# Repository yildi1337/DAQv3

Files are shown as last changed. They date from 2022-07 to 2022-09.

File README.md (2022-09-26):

# DAQv3
A Dual-Channel, Low Noise, Modular, 100 kHz Bandwidth, 24-Bit Data Acquisition (DAQ) Device / FFT Signal Analyzer

# Table of Contents

- **[Introduction](#introduction)**
- **[CAD Model](#cad-model)**
- **[Modules](#modules)**
  - [AnalogConversion_v1](#AnalogConversion_v1)
  - [AnalogConversion_v2](#AnalogConversion_v2)
  - [AnalogConversion_v3](#AnalogConversion_v3)
  - [Backplane_v1](#Backplane_v1)
  - [DigitalBackend_v1](#DigitalBackend_v1)
  - [PowerSupply_5V_v1](#PowerSupply_5V_v1)
  - [PowerSupply_5V_v2](#PowerSupply_5V_v2)
  - [PowerSupply_12V_v1](#PowerSupply_12V_v1)
  - [PowerSupply_12V_v2](#PowerSupply_12V_v2)
  - [USBConnectors_v1](#USBConnectors_v1)
- **[Firmware](#firmware)**
- **[USB Driver](#usb-driver)**
- **[Debug and Control Interface](#debug-and-control-interface)**
- **[Measurement Results](#measurement-results)**
  - [Linear Power Supply vs. Switched-Mode Power Supply](#linear-power-supply-vs-switched-mode-power-supply)
  - [Differential Input Module (AnalogConversion_v3)](#differential-input-module-analogconversion_v3)

# Introduction

Work in progress ...

# CAD Model

The complete CAD model can be downloaded <a href="https://github.com/yildi1337/DAQv3/tree/main/cad_complete/inventor">here</a> (Autodesk Inventor 2023 files) including all <a href="#modules">modules</a> and the case.

<p align="center">
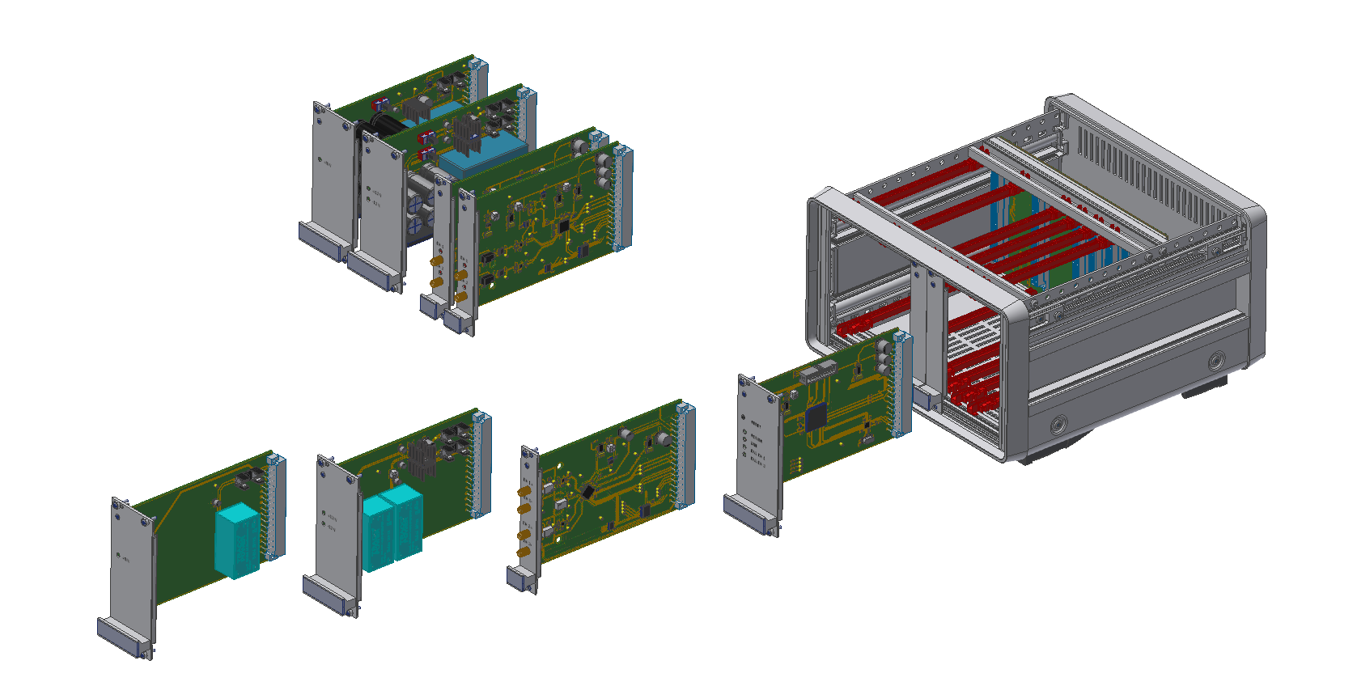
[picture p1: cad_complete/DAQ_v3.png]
    
</p>

# Modules

## AnalogConversion_v1

- [Schematics (PDF)](https://github.com/yildi1337/DAQv3/blob/main/schematics/AnalogConversion_v1_Schematics.pdf)
- [Schematics (Eagle)](https://github.com/yildi1337/DAQv3/blob/main/eagle/AnalogConversion_v1.sch)
- [Board (Eagle)](https://github.com/yildi1337/DAQv3/blob/main/eagle/AnalogConversion_v1.brd)
- [Gerber Files](https://github.com/yildi1337/DAQv3/blob/main/pcb_gerber/AnalogConversion_v1_2022-03-20.zip)
- [3D Step File](https://github.com/yildi1337/DAQv3/blob/main/cad_modules_step/AnalogConversion_v1.step)
- [Bill of Materials](https://github.com/yildi1337/DAQv3/blob/main/pcb_bom/BOM_AnalogConversion_v1.txt)

<p align="center">
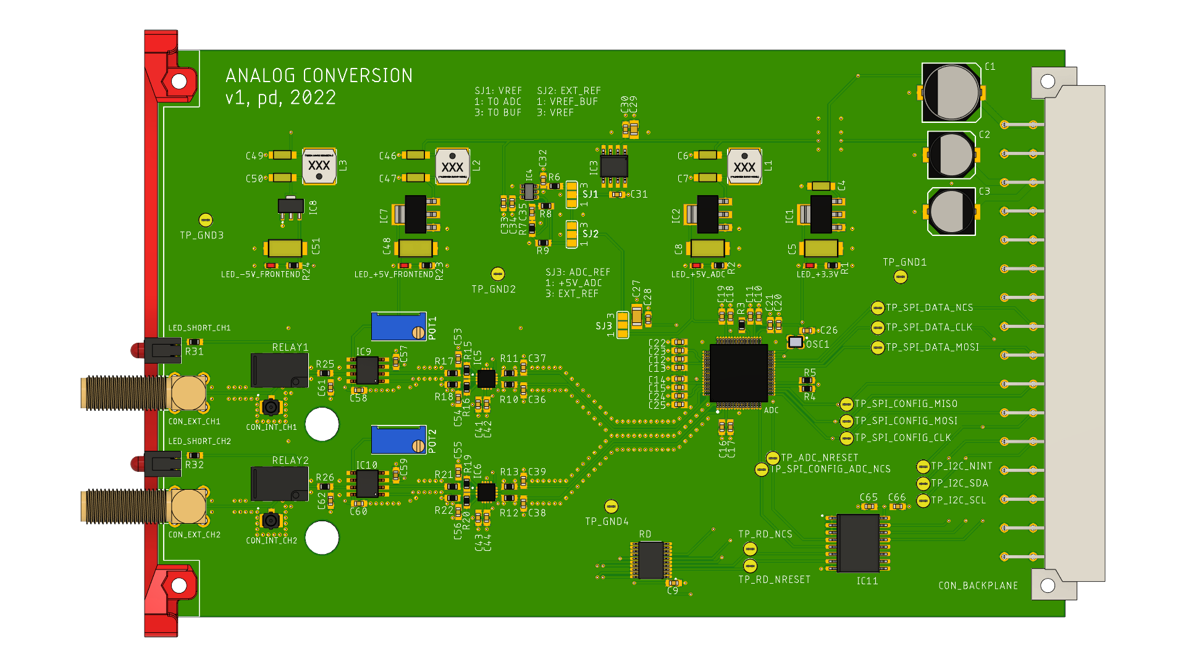
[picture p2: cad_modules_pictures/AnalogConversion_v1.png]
    
</p>

## AnalogConversion_v2

- [Schematics (PDF)](https://github.com/yildi1337/DAQv3/blob/main/schematics/AnalogConversion_v2_Schematics.pdf)
- [Schematics (Eagle)](https://github.com/yildi1337/DAQv3/blob/main/eagle/AnalogConversion_v2.sch)
- [Board (Eagle)](https://github.com/yildi1337/DAQv3/blob/main/eagle/AnalogConversion_v2.brd)
- [Gerber Files](https://github.com/yildi1337/DAQv3/blob/main/pcb_gerber/AnalogConversion_v2_2022-05-25.zip)
- [3D Step File](https://github.com/yildi1337/DAQv3/blob/main/cad_modules_step/AnalogConversion_v2.step)
- [Bill of Materials](https://github.com/yildi1337/DAQv3/blob/main/pcb_bom/BOM_AnalogConversion_v2.txt)

<p align="center">
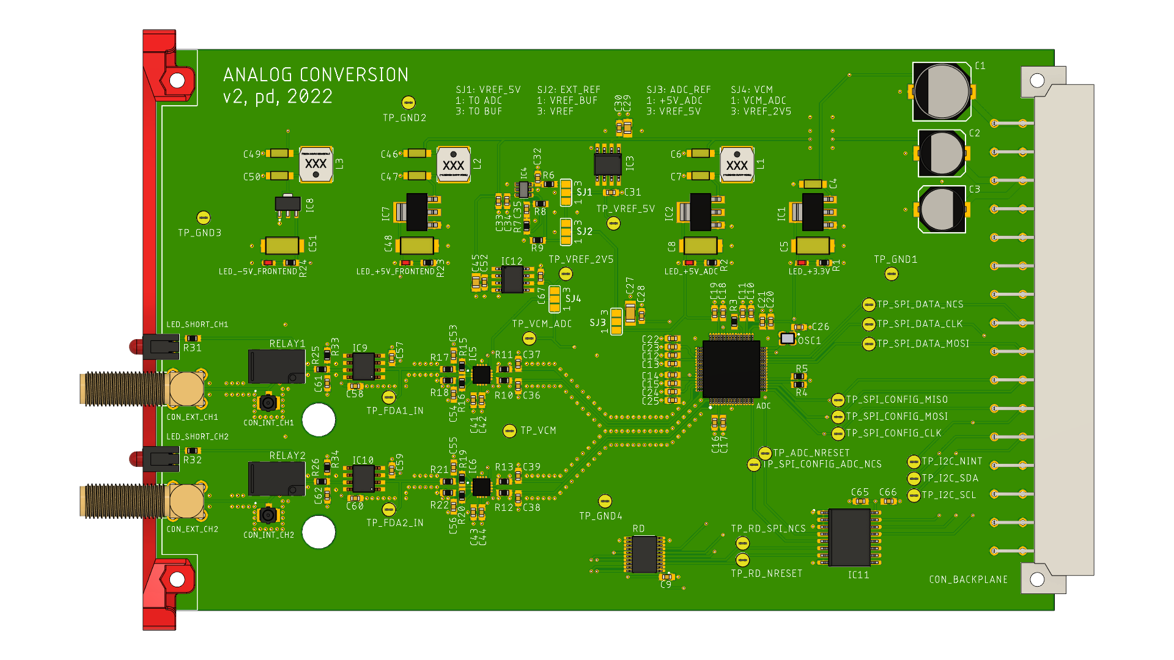
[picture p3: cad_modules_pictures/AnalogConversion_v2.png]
    
</p>

## AnalogConversion_v3

- [Schematics (PDF)](https://github.com/yildi1337/DAQv3/blob/main/schematics/AnalogConversion_v3_Schematics.pdf)
- [Schematics (Eagle)](https://github.com/yildi1337/DAQv3/blob/main/eagle/AnalogConversion_v3.sch)
- [Board (Eagle)](https://github.com/yildi1337/DAQv3/blob/main/eagle/AnalogConversion_v3.brd)
- [Gerber Files](https://github.com/yildi1337/DAQv3/blob/main/pcb_gerber/AnalogConversion_v3_2022-07-25.zip)
- [3D Step File](https://github.com/yildi1337/DAQv3/blob/main/cad_modules_step/AnalogConversion_v3.step)
- [Bill of Materials](https://github.com/yildi1337/DAQv3/blob/main/pcb_bom/BOM_AnalogConversion_v3.txt)

<p align="center">
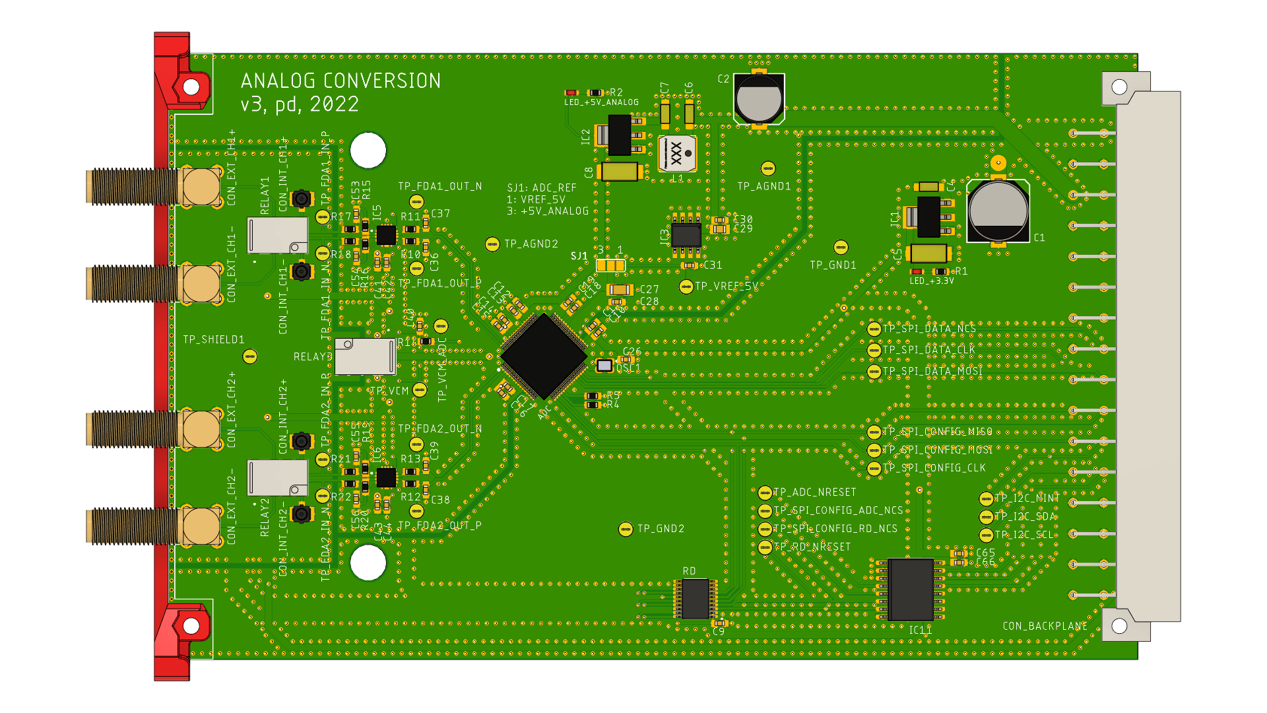
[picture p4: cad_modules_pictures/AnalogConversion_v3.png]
    
</p>

## Backplane_v1

- [Schematics (PDF)](https://github.com/yildi1337/DAQv3/blob/main/schematics/Backplane_v1_Schematics.pdf)
- [Schematics (Eagle)](https://github.com/yildi1337/DAQv3/blob/main/eagle/Backplane_v1.sch)
- [Board (Eagle)](https://github.com/yildi1337/DAQv3/blob/main/eagle/Backplane_v1.brd)
- [Gerber Files](https://github.com/yildi1337/DAQv3/blob/main/pcb_gerber/Backplane_v1_2022-03-20.zip)
- [3D Step File](https://github.com/yildi1337/DAQv3/blob/main/cad_modules_step/Backplane_v1.step)
- [Bill of Materials](https://github.com/yildi1337/DAQv3/blob/main/pcb_bom/BOM_Backplane_v1.txt)

<p align="center">
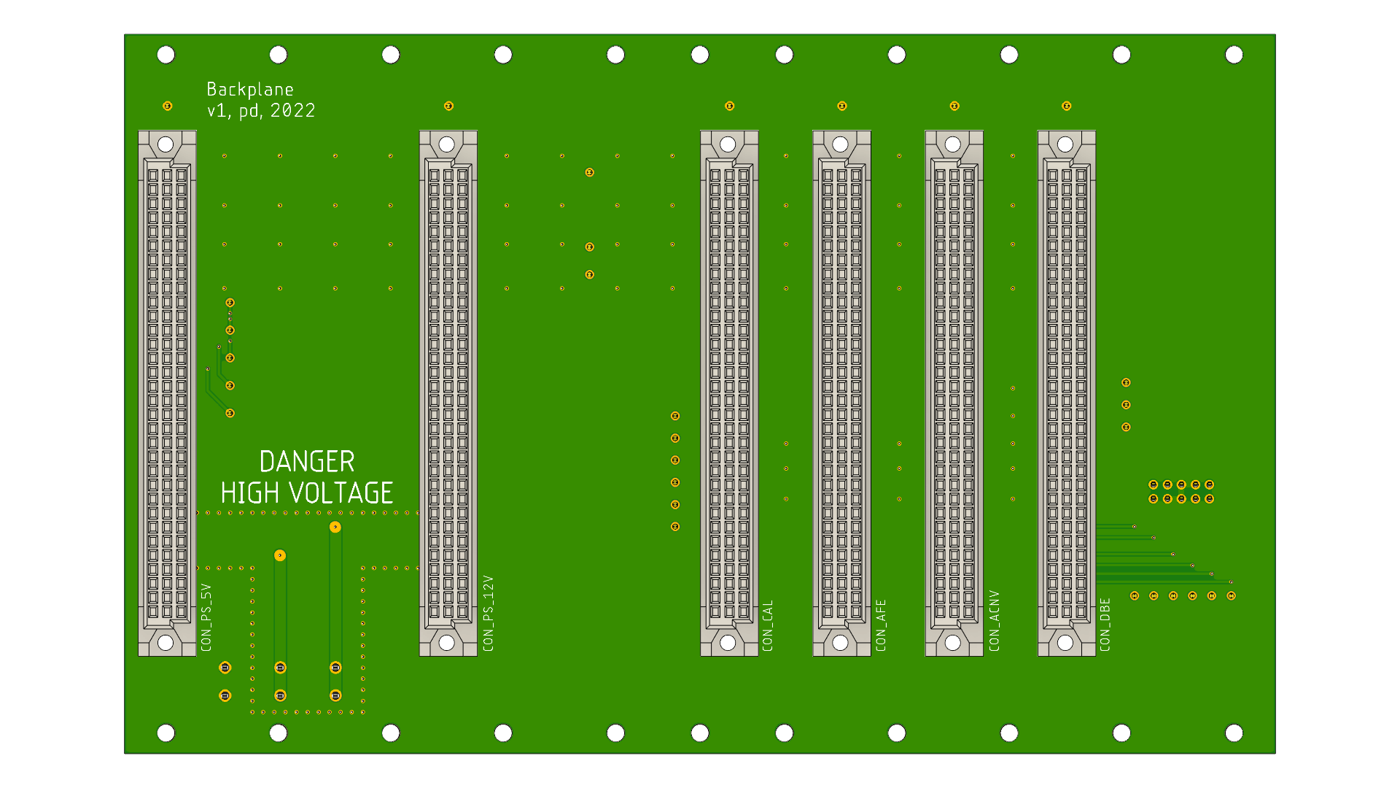
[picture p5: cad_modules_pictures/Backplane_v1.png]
    
</p>

## DigitalBackend_v1

- [Schematics (PDF)](https://github.com/yildi1337/DAQv3/blob/main/schematics/DigitalBackend_v1_Schematics.pdf)
- [Schematics (Eagle)](https://github.com/yildi1337/DAQv3/blob/main/eagle/DigitalBackend_v1.sch)
- [Board (Eagle)](https://github.com/yildi1337/DAQv3/blob/main/eagle/DigitalBackend_v1.brd)
- [Gerber Files](https://github.com/yildi1337/DAQv3/blob/main/pcb_gerber/DigitalBackend_v1_2022-03-20.zip)
- [3D Step File](https://github.com/yildi1337/DAQv3/blob/main/cad_modules_step/DigitalBackend_v1.step)
- [Bill of Materials](https://github.com/yildi1337/DAQv3/blob/main/pcb_bom/BOM_DigitalBackend_v1.txt)

<p align="center">
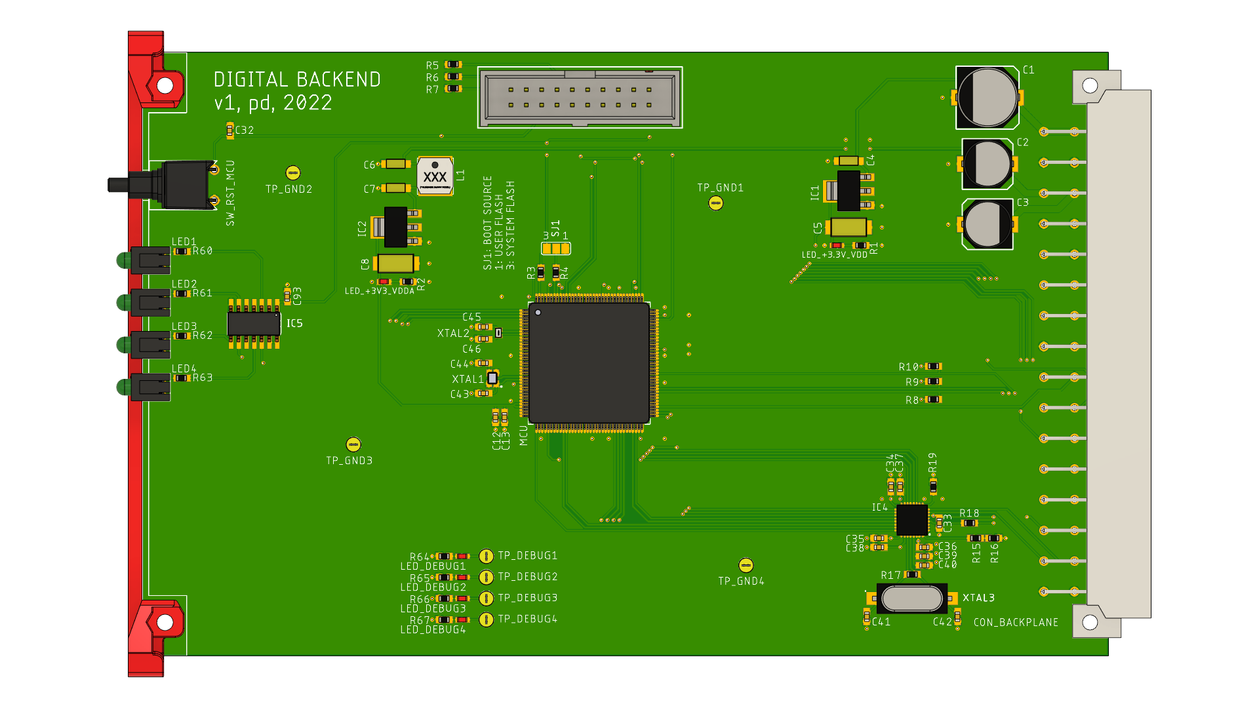
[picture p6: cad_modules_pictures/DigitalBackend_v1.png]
    
</p>

## PowerSupply_12V_v1

- [Schematics (PDF)](https://github.com/yildi1337/DAQv3/blob/main/schematics/PowerSupply_12V_v1_Schematics.pdf)
- [Schematics (Eagle)](https://github.com/yildi1337/DAQv3/blob/main/eagle/PowerSupply_12V_v1.sch)
- [Board (Eagle)](https://github.com/yildi1337/DAQv3/blob/main/eagle/PowerSupply_12V_v1.brd)
- [Gerber Files](https://github.com/yildi1337/DAQv3/blob/main/pcb_gerber/PowerSupply_12V_v1_2022-03-20.zip)
- [3D Step File](https://github.com/yildi1337/DAQv3/blob/main/cad_modules_step/PowerSupply_12V_v1.step)
- [Bill of Materials](https://github.com/yildi1337/DAQv3/blob/main/pcb_bom/BOM_PowerSupply_12V_v1.txt)

<p align="center">
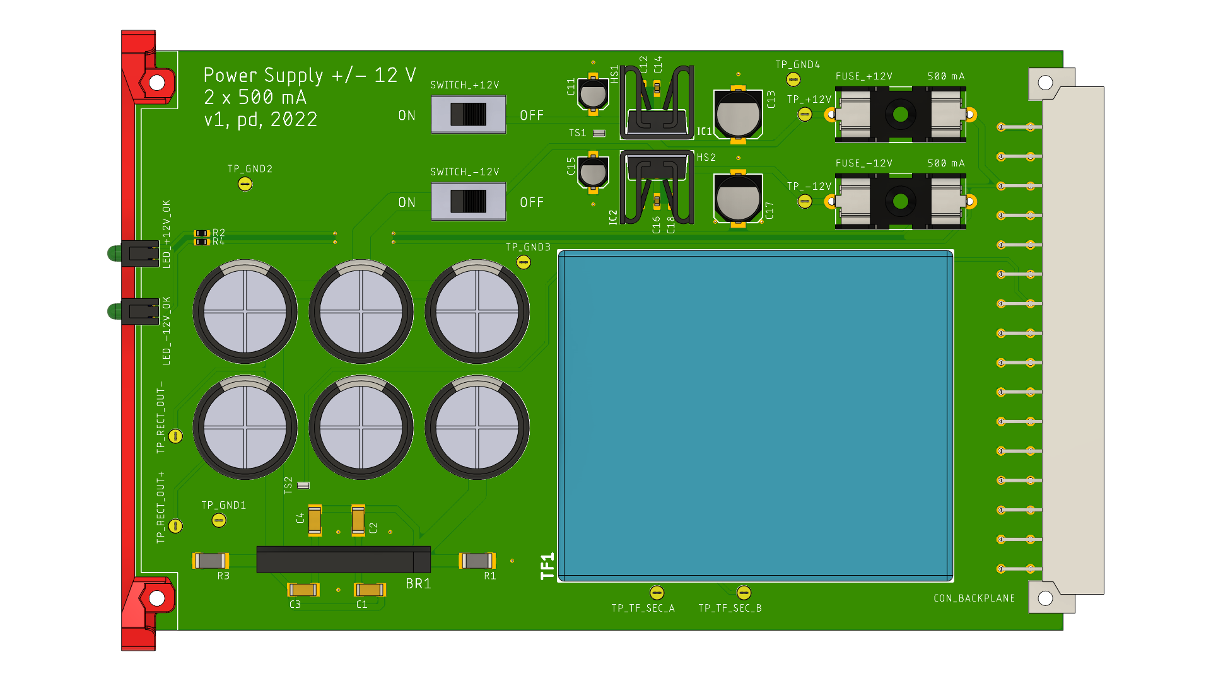
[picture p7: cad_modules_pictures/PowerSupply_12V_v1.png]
    
</p>

## PowerSupply_12V_v2

- [Schematics (PDF)](https://github.com/yildi1337/DAQv3/blob/main/schematics/PowerSupply_12V_v2_Schematics.pdf)
- [Schematics (Eagle)](https://github.com/yildi1337/DAQv3/blob/main/eagle/PowerSupply_12V_v2.sch)
- [Board (Eagle)](https://github.com/yildi1337/DAQv3/blob/main/eagle/PowerSupply_12V_v2.brd)
- [Gerber Files](https://github.com/yildi1337/DAQv3/blob/main/pcb_gerber/PowerSupply_12V_v2_2022-05-25.zip)
- [3D Step File](https://github.com/yildi1337/DAQv3/blob/main/cad_modules_step/PowerSupply_12V_v2.step)
- [Bill of Materials](https://github.com/yildi1337/DAQv3/blob/main/pcb_bom/BOM_PowerSupply_12V_v2.txt)

<p align="center">
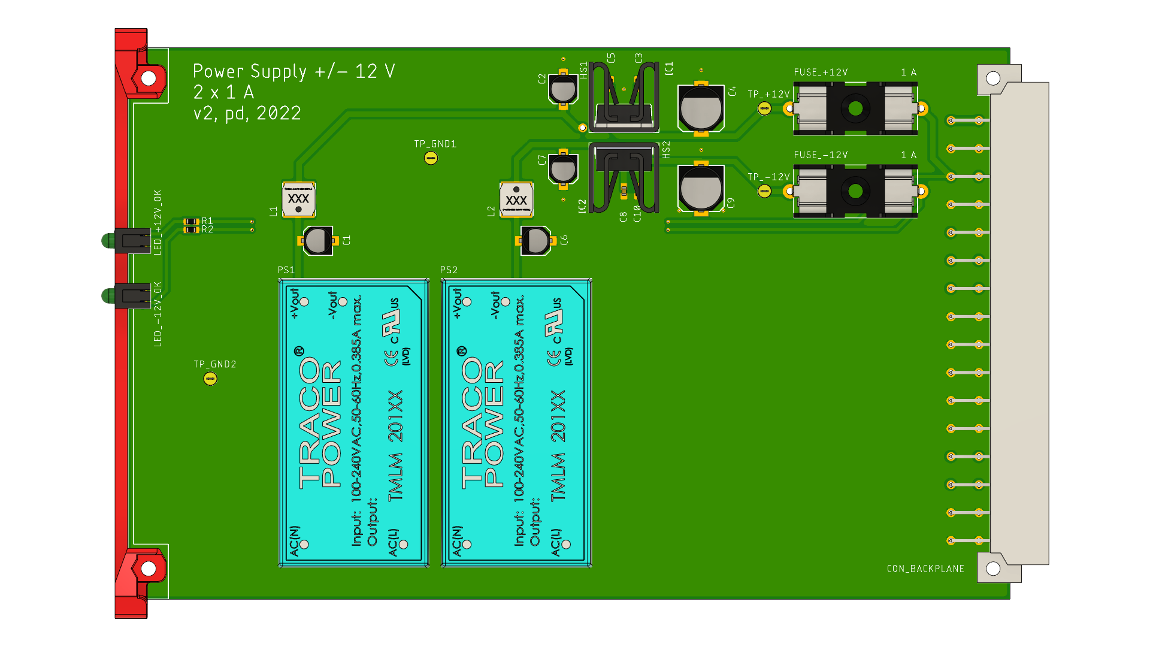
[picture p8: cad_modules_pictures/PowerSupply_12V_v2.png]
    
</p>

## PowerSupply_5V_v1

- [Schematics (PDF)](https://github.com/yildi1337/DAQv3/blob/main/schematics/PowerSupply_5V_v1_Schematics.pdf)
- [Schematics (Eagle)](https://github.com/yildi1337/DAQv3/blob/main/eagle/PowerSupply_5V_v1.sch)
- [Board (Eagle)](https://github.com/yildi1337/DAQv3/blob/main/eagle/PowerSupply_5V_v1.brd)
- [Gerber Files](https://github.com/yildi1337/DAQv3/blob/main/pcb_gerber/PowerSupply_5V_v1_2022-03-20.zip)
- [3D Step File](https://github.com/yildi1337/DAQv3/blob/main/cad_modules_step/PowerSupply_5V_v1.step)
- [Bill of Materials](https://github.com/yildi1337/DAQv3/blob/main/pcb_bom/BOM_PowerSupply_5V_v1.txt)

<p align="center">
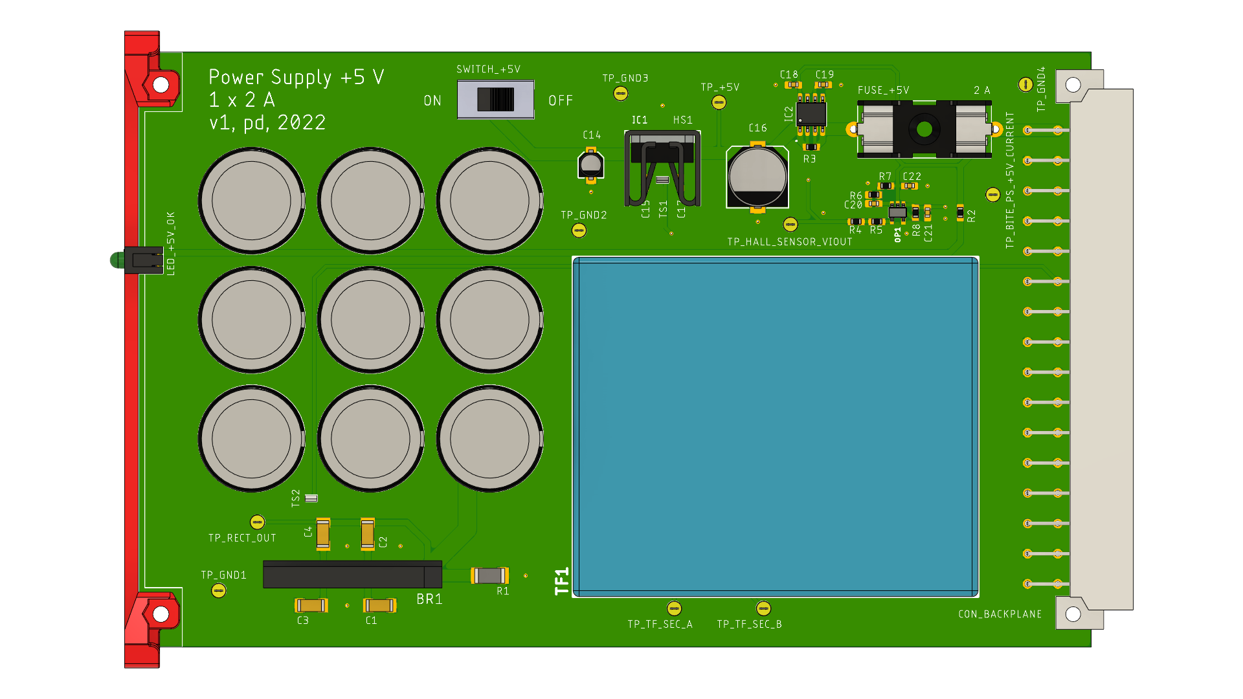
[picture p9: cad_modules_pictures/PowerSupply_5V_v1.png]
    
</p>

## PowerSupply_5V_v2

- [Schematics (PDF)](https://github.com/yildi1337/DAQv3/blob/main/schematics/PowerSupply_5V_v2_Schematics.pdf)
- [Schematics (Eagle)](https://github.com/yildi1337/DAQv3/blob/main/eagle/PowerSupply_5V_v2.sch)
- [Board (Eagle)](https://github.com/yildi1337/DAQv3/blob/main/eagle/PowerSupply_5V_v2.brd)
- [Gerber Files](https://github.com/yildi1337/DAQv3/blob/main/pcb_gerber/PowerSupply_5V_v2_2022-05-25.zip)
- [3D Step File](https://github.com/yildi1337/DAQv3/blob/main/cad_modules_step/PowerSupply_5V_v2.step)
- [Bill of Materials](https://github.com/yildi1337/DAQv3/blob/main/pcb_bom/BOM_PowerSupply_5V_v2.txt)

<p align="center">
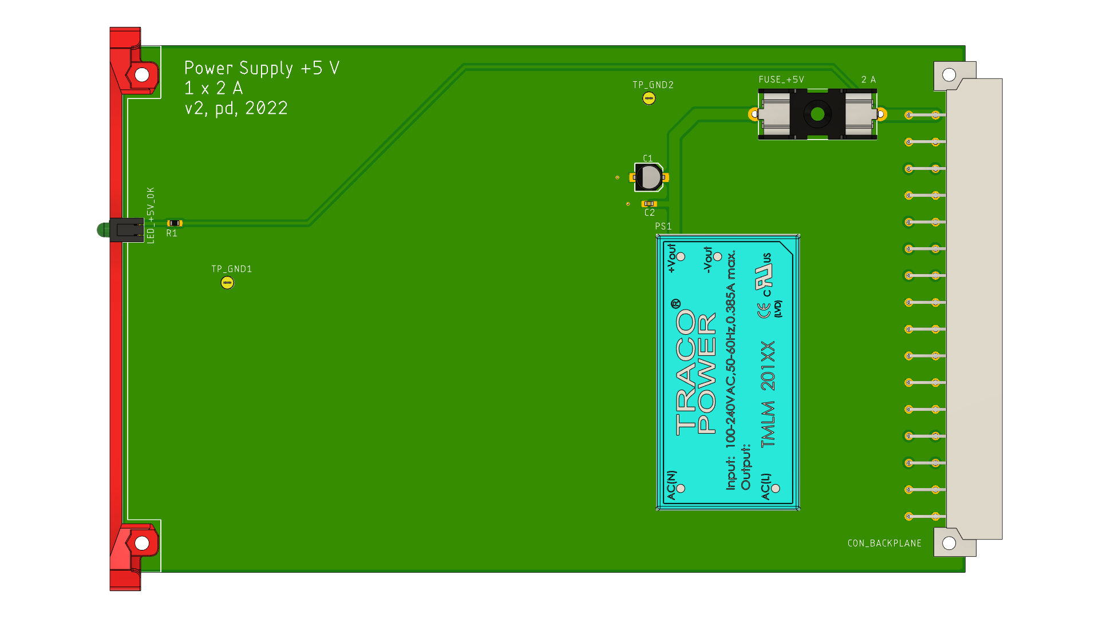
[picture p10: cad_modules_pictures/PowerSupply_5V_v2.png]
    
</p>

## USBConnectors_v1

- [Schematics (PDF)](https://github.com/yildi1337/DAQv3/blob/main/schematics/USBConnectors_v1_Schematics.pdf)
- [Schematics (Eagle)](https://github.com/yildi1337/DAQv3/blob/main/eagle/USBConnectors_v1.sch)
- [Board (Eagle)](https://github.com/yildi1337/DAQv3/blob/main/eagle/USBConnectors_v1.brd)
- [Gerber Files](https://github.com/yildi1337/DAQv3/blob/main/pcb_gerber/USBConnectors_v1_2022-03-14.zip)
- [3D Step File](https://github.com/yildi1337/DAQv3/blob/main/cad_modules_step/USBConnectors_v1.step)
- [Bill of Materials](https://github.com/yildi1337/DAQv3/blob/main/pcb_bom/BOM_USBConnectors_v1.txt)

<p align="center">
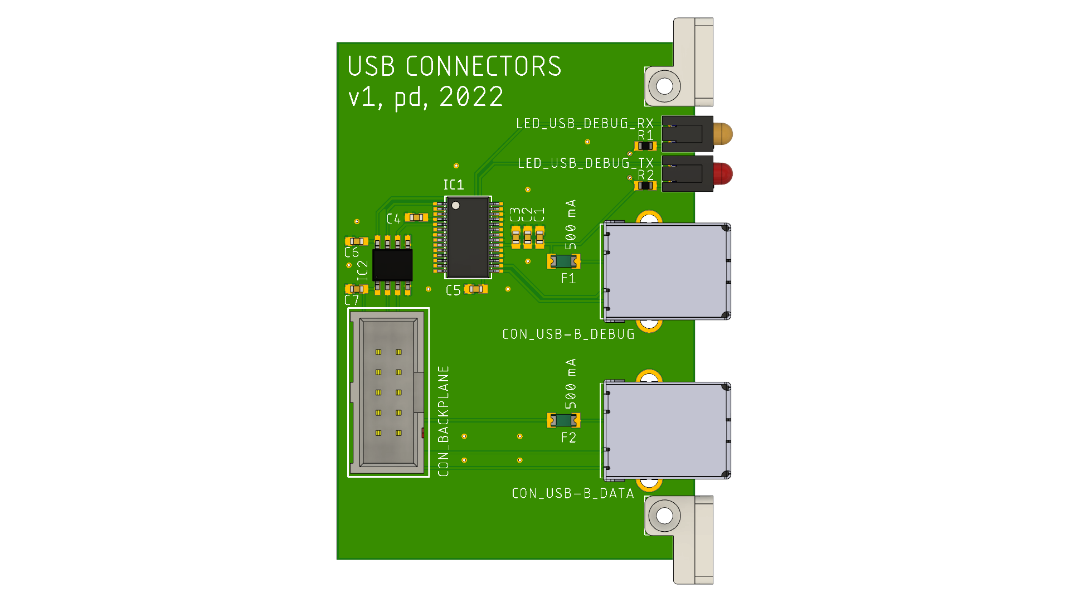
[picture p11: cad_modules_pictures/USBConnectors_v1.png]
    
</p>

# Firmware

The firmware running on the STM32H753ZIT6 is mainly written in ANSI C and has been developed in <a href="https://www.st.com/en/development-tools/stm32cubeide.html">STM32CubeIDE</a> version 1.10.1 utilizing the official <a href="https://github.com/STMicroelectronics/stm32h7xx_hal_driver">STM32H7xx_HAL_Driver</a>. Among others, the firmware performs the following tasks:

- Configuration of the ADC AD7768 (on module <a href="#AnalogConversion_v3">AnalogConversion_v3</a>) via SPI (SPI_3).
- Reception of sampled data from the ADC AD7768 via SPI (SPI_2) and DMA (DMA1_Stream0).
- Transmission of sampled data from the ADC AD7768 via USB 2.0 Hi-Speed to the PC utilizing ULPI interface and an additional Hi-Speed USB PHY (USB3300).
- Handling USART connection (USART_1, via FT232RL chip on <a href="#USBConnectors_v1">USBConnectors_v1</a>) for debug purposes and for exchanging control/status commands with the PC.
- Controlling I2C bus (I2C_4) for controlling I/O expander TCA9534A (e.g. on module <a href="#AnalogConversion_v3">AnalogConversion_v3</a>) which, in turn, drives a relay driver (MAX4820) on the same module.
- Controlling front LEDs (on module <a href="#DigitalBackend_v1">DigitalBackend_v1</a>).

The complete source code can be found <a href="https://github.com/yildi1337/DAQv3/tree/main/firmware">here</a>.

# USB Driver

Two USB drivers are needed for operating the DAQ v3:

- For the reception of the sampled data from the ADC NI-VISA is utilized. The driver matching the hardware of this project has been generated with the NI-VISA Driver Wizard an can be downloaded <a href="https://github.com/yildi1337/DAQv3/tree/main/usb_driver/ni-visa">here</a>.
- To use the USB debug interface only the official USB serial driver from FTDI is required, which can be downloaded <a href="https://github.com/yildi1337/DAQv3/tree/main/usb_driver/ftdi">here</a>.

# Debug and Control Interface

Tool for graphical display of status information and for controlling the hardware via the virtual serial interface (second USB-B port). The python source code and a binary (only tested on x64 Microsoft Windows 10) can be downloaded <a href="https://github.com/yildi1337/DAQv3/tree/main/debug_interface">here</a>. 

<p align="center">
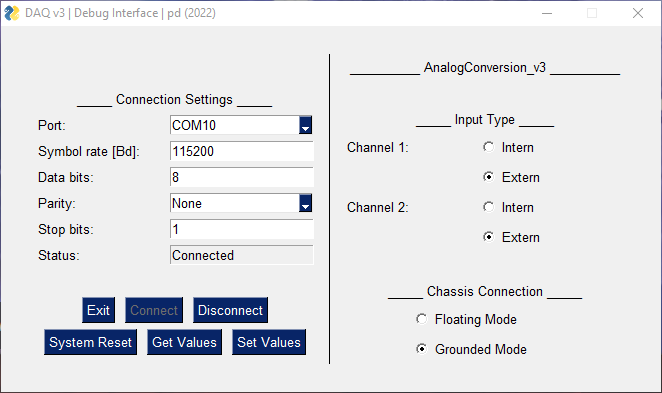
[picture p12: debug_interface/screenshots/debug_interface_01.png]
    
</p>

# Measurement Results

## Linear Power Supply vs. Switched-Mode Power Supply

Noise measurements (60 seconds) were performed while powering the electronics with the power supplies of versions v1 and v2, where the abbreviations PS and ACNV in the titles refer to the power supply and analog conversion modules.

The two linear power supply modules of version v1 both operate with transformers. This resulted in heavy magnetic interference in the form of the mains frequency and multiples thereof.

The two power supply modules of version v2 both operate with AC/DC power modules (<a href="https://www.tracopower.com/de/deu/model/tmlm-20105">TMLM 20105</a>, <a href="https://www.tracopower.com/de/deu/model/tmlm-20115">TMLM 20115</a>) from Traco Power. Their switching frequencies are around 132 +/- 8 kHz and thus above the useful range of 0 - 100 kHz (Nyquist frequency is 128 kHz).

<p align="center">
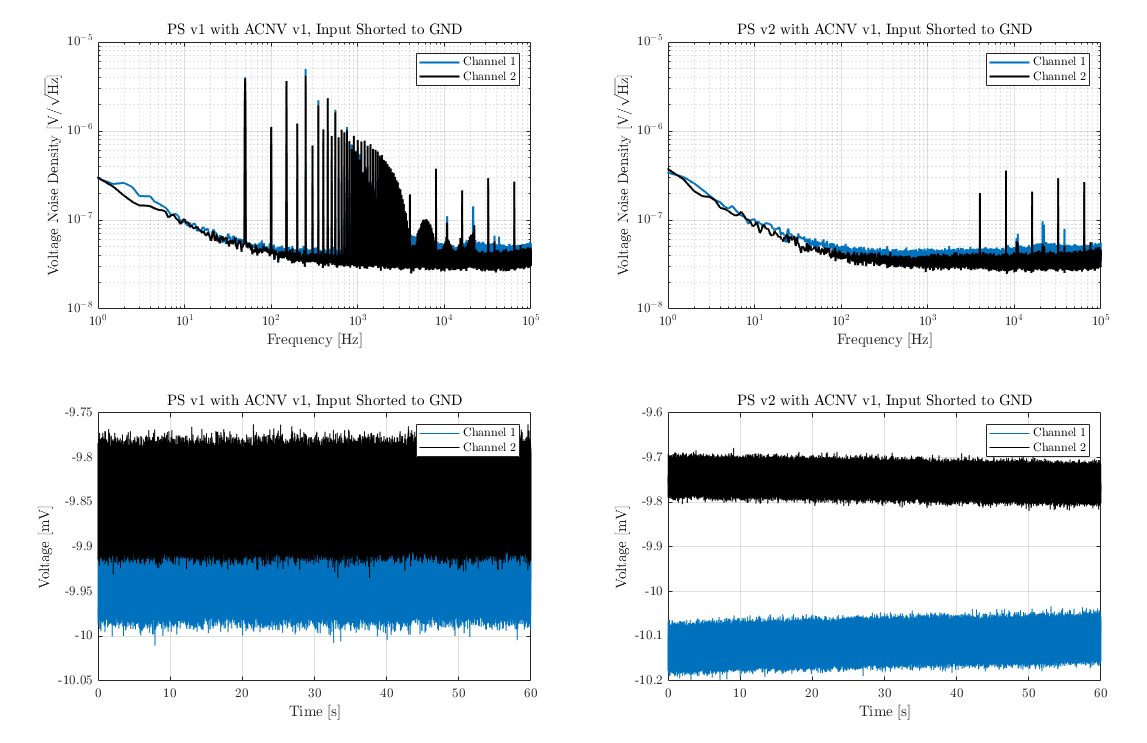
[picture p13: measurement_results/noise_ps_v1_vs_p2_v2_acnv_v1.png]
    
</p>

## Differential Input Module (AnalogConversion_v3)

The investigated setup consists of the modules:

- <a href="#Backplane_v1">Backplane_v1</a>
- <a href="#PowerSupply_5V_v2">PowerSupply_5V_v2</a>
- <a href="#PowerSupply_12V_v2">PowerSupply_12V_v2</a>
- <a href="#AnalogConversion_v3">AnalogConversion_v3</a>
- <a href="#DigitalBackend_v1">DigitalBackend_v1</a>
- <a href="#USBConnectors_v1">USBConnectors_v1</a>

### Mains Interference and Grounding

The two differential inputs of each channel were connected via <a href="https://www.mouser.de/ProductDetail/Amphenol-RF/132360?qs=V8V9vCxO5JtDrelx3RqrVA%3D%3D">50 Ohm SMA resistors</a> with AGND (SHIELD connected via R6 = 0 Ohm with AGND, <a href="https://github.com/yildi1337/DAQv3/blob/main/schematics/AnalogConversion_v3_Schematics.pdf">see schematics</a>).

<p align="center">
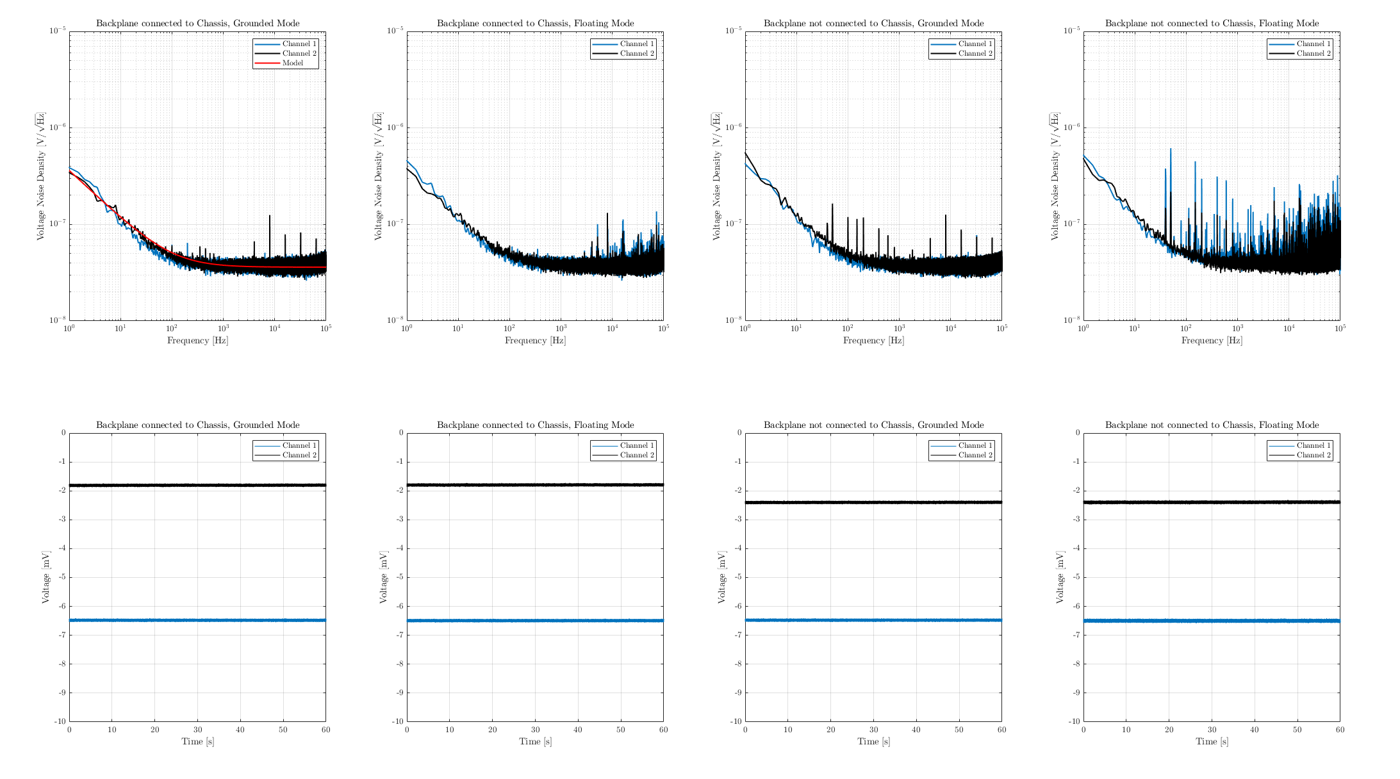
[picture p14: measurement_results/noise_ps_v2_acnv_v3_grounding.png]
    
</p>

Obviously, the lowest interference occurs in grounded mode and when GND of the backplane is directly connected to the chassis/the protective earth connector of the power entry module (first plot).

### Input Noise of Differential Opamp Driver and ADC

The measurement result from above is essential for the further development of the preamplifier. The gain of the preamplifier must be high enough to be able to neglect the noise from the opamp driver (ADA4945-1) and ADC (AD7768-4) determined here. A useful model for describing the power spectral density of the voltage noise $PSD(f)$ (in units of $\mathrm{V}^2/\mathrm{Hz}$) is the polynomial law 
$$\mathrm{PSD}(f) = \mathrm{LSD}^2(f) = \sum_{i=-1}^{0} b_i f^i$$ 
where $i=0$ and $i=-1$ refer to white noise and $1/f$ flicker noise, respectively, and $\mathrm{LSD}(f)$ referes to the linear spectrum density (in units of $\mathrm{V}/\sqrt{\mathrm{Hz}}$). For this measurement, values of
- $b_{-1} = 1.3 \cdot 10^{-13}~\mathrm{V}^2$
- $b_0 = {1.3 \cdot 10^{-15}~\mathrm{V}^2/\mathrm{Hz}}$
were found.

This results in a $1/f$ corner frequency of $f_{\mathrm{c}} = b_{-1}/b_0 = 100~\mathrm{Hz}$. The white voltage noise density is equal to $\sqrt{b_0} = 36~\mathrm{nV}/\sqrt{\mathrm{Hz}}$. Based on the two time domain noise signals RMS noise values of $13.2~\mu\mathrm{V}$ (channel 1) and $13.5~\mu\mathrm{V}$ (channel 2) were determined after substracting the DC offsets of $-6.5~\mathrm{mV}$ and $-1.8~\mathrm{mV}$.

The measured RMS noise values are in good agreement with the value of $11.58~\mu\mathrm{V}$ given in the datasheet (for the ADC only).

<p align="center">
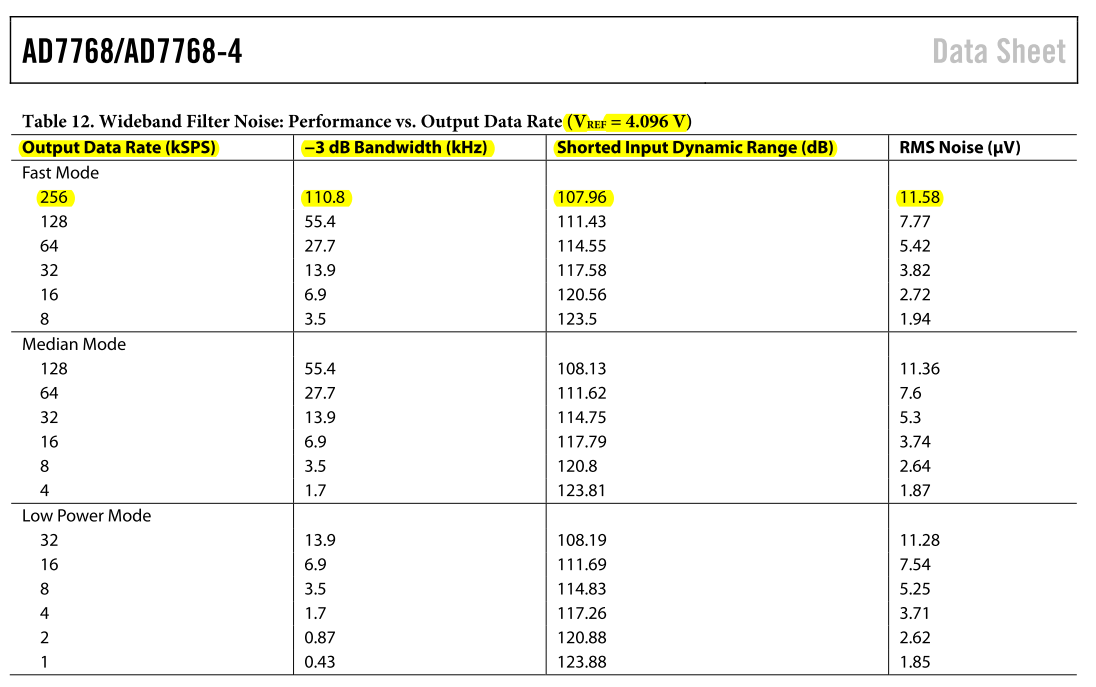
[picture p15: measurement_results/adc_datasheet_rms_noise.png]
    
</p>

In addition, for $V_{\mathrm{ref}} = 5~\mathrm{V}$, the dynamic range of the utilized combination of opamp driver and ADC is better than 

$$\mathrm{DR} = 20 \cdot \log_{10}\left(\frac{2 \cdot V_{\mathrm{ref}}}{\sqrt{2} \cdot \mathrm{RMS}\ \mathrm{noise}}\right)~\mathrm{dB} = 114\ \mathrm{dB}$$ 

### ADC RAW Data for Several Input Configurations

<p align="center">
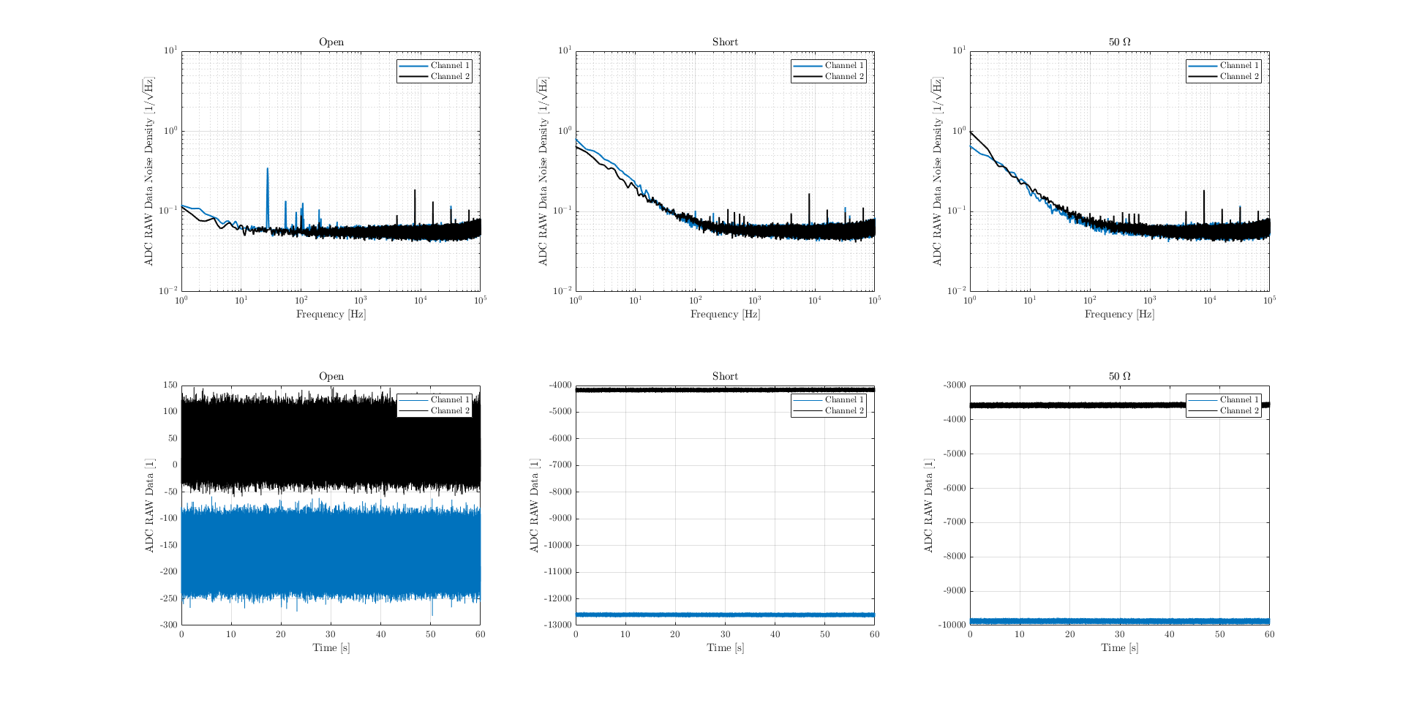
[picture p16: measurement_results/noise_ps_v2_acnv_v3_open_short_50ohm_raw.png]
    
</p>

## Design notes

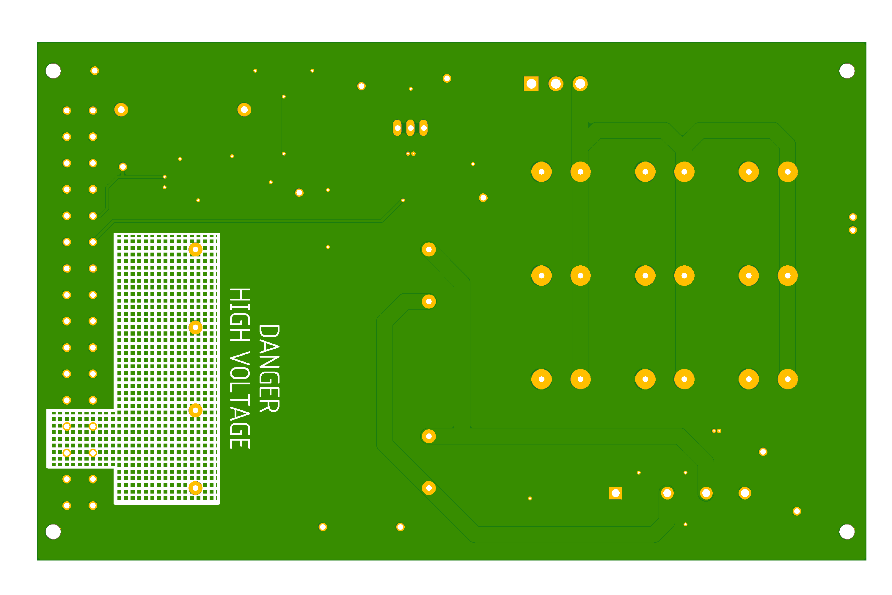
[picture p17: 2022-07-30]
pcb_pictures_boards/PowerSupply_5V_v1_PCB_Bottom.png

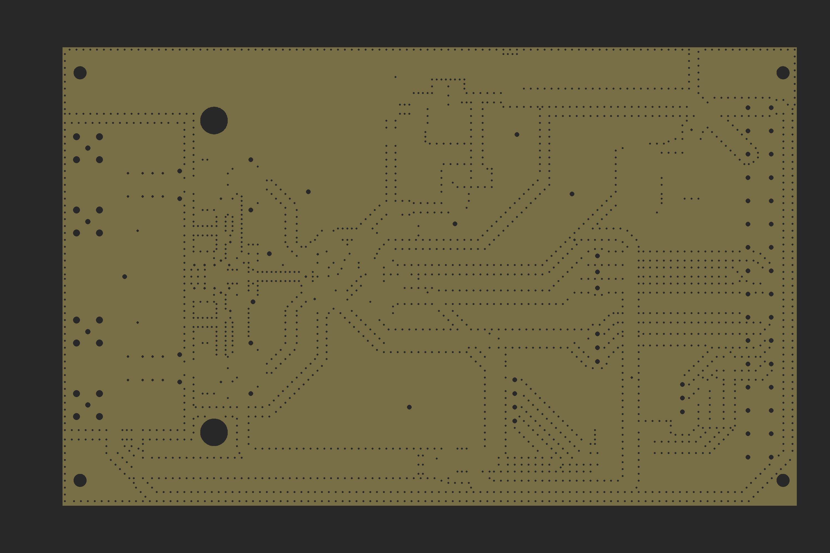
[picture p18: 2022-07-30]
pcb_pictures_boards/AnalogConversion_v3_PCB_Drills.png

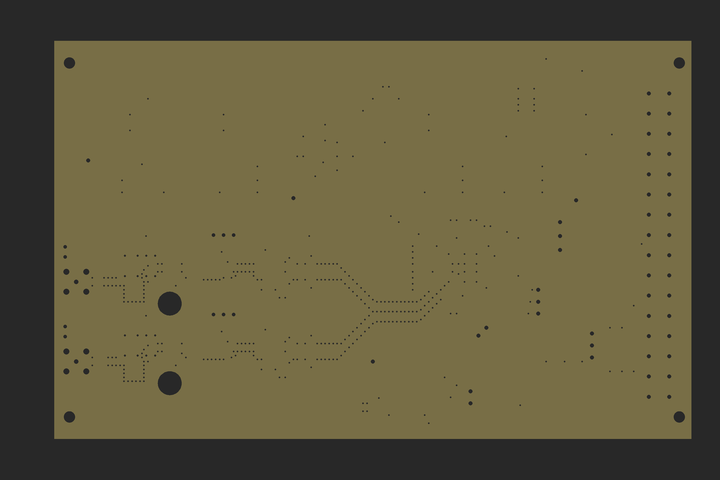
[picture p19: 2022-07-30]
pcb_pictures_boards/AnalogConversion_v1_PCB_Drills.png

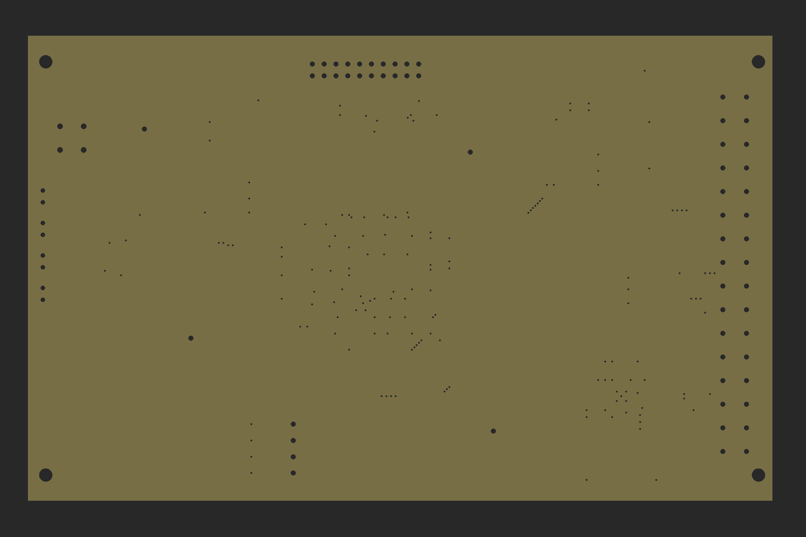
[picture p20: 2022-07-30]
pcb_pictures_boards/DigitalBackend_v1_PCB_Drills.png

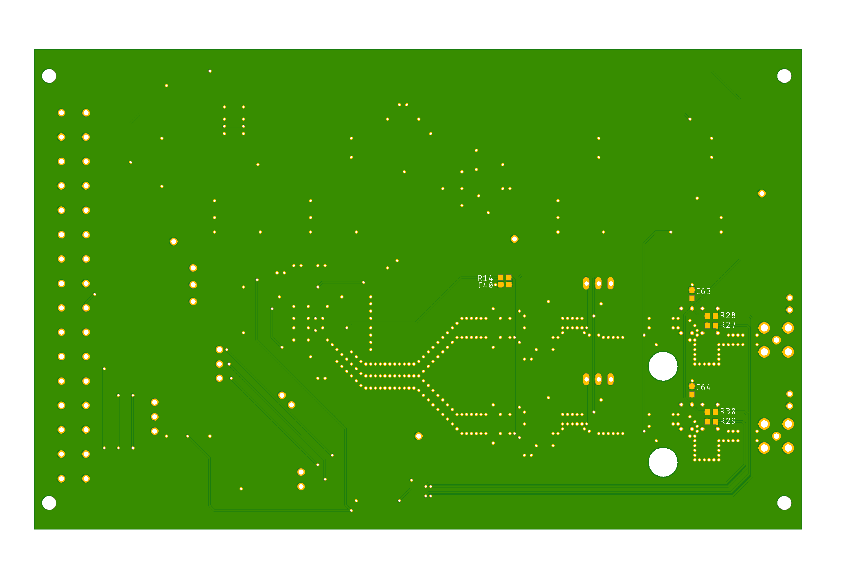
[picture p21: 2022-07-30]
pcb_pictures_boards/AnalogConversion_v1_PCB_Bottom.png

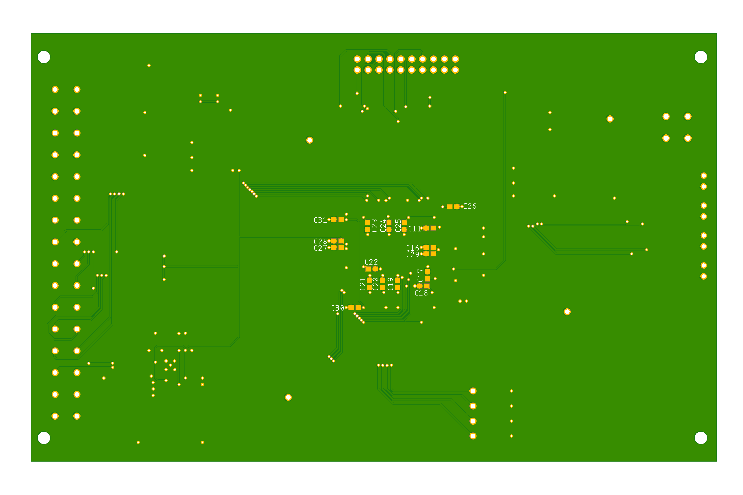
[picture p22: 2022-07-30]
pcb_pictures_boards/DigitalBackend_v1_PCB_Bottom.png

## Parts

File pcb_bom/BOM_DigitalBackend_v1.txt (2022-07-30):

Qty Value                           Device                          Package                         Parts                                                                                                   Description                          POPULARITY SPICEPREFIX
6                                   LEDCHIP-LED0603                 CHIP-LED0603                    LED_+3.3V_VDD, LED_+3V3_VDDA, LED_DEBUG1, LED_DEBUG2, LED_DEBUG3, LED_DEBUG4                            LED                                  26                    
4                                   RSPRO-1MM-TERMINAL-POST-2622034 RSPRO-1MM-TERMINAL-POST-2622034 TP_GND1, TP_GND2, TP_GND3, TP_GND4                                                                                                                                 
1                                   SJ2W                            SJ_2                            SJ1                                                                                                     SMD solder JUMPER                    7                     
1   09031326921                     09031326921                     09031326921                     CON_BACKPLANE                                                                                                                                                      
3   1.5k                            R-EU_R0603                      R0603                           R8, R9, R10                                                                                             RESISTOR, European symbol            70         R          
1   1.8k                            R-EU_R0603                      R0603                           R2                                                                                                      RESISTOR, European symbol            70         R          
1   1000u/16V                       CPOL-EU153CLV-1010              153CLV-1010                     C1                                                                                                      POLARIZED CAPACITOR, European symbol 0          C          
21  100n                            C-EUC0603                       C0603                           C13, C16, C17, C18, C19, C20, C21, C22, C23, C24, C25, C26, C28, C32, C33, C34, C35, C36, C37, C40, C93 CAPACITOR, European symbol           73         C          
1   100u                            VLS6045AF-101M                  VLS6045AF-101M                  L1                                                                                                                                                                 
2   100u/25V                        CPOL-EU153CLV-0810              153CLV-0810                     C2, C3                                                                                                  POLARIZED CAPACITOR, European symbol 4          C          
6   10k                             R-EU_R0603                      R0603                           R3, R4, R5, R6, R7, R16                                                                                 RESISTOR, European symbol            70         R          
3   10u                             CPOL-EUCT3216                   CT3216                          C4, C6, C7                                                                                              POLARIZED CAPACITOR, European symbol 1          C          
4   113-314-04                      113-314-04                      113-314-04                      LED1, LED2, LED3, LED4                                                                                                                                             
2   15p                             C-EUC0603                       C0603                           C45, C46                                                                                                CAPACITOR, European symbol           73         C          
1   1M                              R-EU_R0603                      R0603                           R17                                                                                                     RESISTOR, European symbol            70         R          
3   1u                              C-EUC0603                       C0603                           C11, C12, C27                                                                                           CAPACITOR, European symbol           73         C          
2   2.2u                            C-EUC0603                       C0603                           C30, C31                                                                                                CAPACITOR, European symbol           73         C          
2   22u                             CPOL-EUCT6032                   CT6032                          C5, C8                                                                                                  POLARIZED CAPACITOR, European symbol 2          C          
2   27p                             C-EUC0603                       C0603                           C41, C42                                                                                                CAPACITOR, European symbol           73         C          
1   2k                              R-EU_R0603                      R0603                           R15                                                                                                     RESISTOR, European symbol            70         R          
1   4.7k                            R-EU_R0603                      R0603                           R19                                                                                                     RESISTOR, European symbol            70         R          
3   4.7u                            C-EUC0603                       C0603                           C29, C38, C39                                                                                           CAPACITOR, European symbol           73         C          
2   5.6p                            C-EUC0603                       C0603                           C43, C44                                                                                                CAPACITOR, European symbol           73         C          
1   60807-011                       60807-011                       60807-011                       PCB_BRACKET                                                                                                                                                        
4   68                              R-EU_R0603                      R0603                           R60, R61, R62, R63                                                                                      RESISTOR, European symbol            70         R          
1   74LVC126AD,112                  74AC126D                        SO14                            IC5                                                                                                     Quad bus BUFFER, 3-state             0                     
5   750                             R-EU_R0603                      R0603                           R1, R64, R65, R66, R67                                                                                  RESISTOR, European symbol            70         R          
1   820                             R-EU_R0603                      R0603                           R18                                                                                                     RESISTOR, European symbol            70         R          
1   ABS05-32.768KHZ-T               ABS05-32.768KHZ-T               ABS05-32.768KHZ-T               XTAL2                                                                                                                                                              
1   FOXSDLF-240F-20                 FOXSDLF-240F-20                 FOXSDLF-240F-20                 XTAL3                                                                                                                                                              
2   LM1117IMP-3.3                   LM1117IMPX-3.3                  SOT223                          IC1, IC2                                                                                                                                                           
4   RSPRO-1MM-TERMINAL-POST-2622034 RSPRO-1MM-TERMINAL-POST-2622034 RSPRO-1MM-TERMINAL-POST-2622034 TP_DEBUG1, TP_DEBUG2, TP_DEBUG3, TP_DEBUG4                                                                                                                         
1   STM32H753ZIT6                   STM32H753ZIT6                   LQFP144                         MCU                                                                                                                                                                
1   TP33W008000                     TP33W008000                     TP33W008000                     SW_RST_MCU                                                                                                                                                         
1   TST-110-01-T-DJ                 TST-110-01-T-DJ                 TST-110-01-T-D                  CON_JTAG                                                                                                                                                           
1   USB3300-EZK                     USB3300-EZK                     USB3300-EZK                     IC4                                                                                                                                                                
1   XRCGB25M000F2P00R0              XRCGB25M000F2P00R0              XRCGB25M000F2P00R0              XTAL1

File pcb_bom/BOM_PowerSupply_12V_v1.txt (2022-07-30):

Qty Value                           Device                          Package                         Parts                                                                                                      Description                          POPULARITY SPICEPREFIX
10                                  RSPRO-1MM-TERMINAL-POST-2622034 RSPRO-1MM-TERMINAL-POST-2622034 TP_+12V, TP_-12V, TP_GND1, TP_GND2, TP_GND3, TP_GND4, TP_RECT_OUT+, TP_RECT_OUT-, TP_TF_SEC_A, TP_TF_SEC_B                                                            
2   0031.8201                       0031.8201                       0031.8201                       FUSE_+12V, FUSE_-12V                                                                                                                                                  
1   09031326921                     09031326921                     09031326921                     CON_BACKPLANE                                                                                                                                                         
6   10000u/25V                      EEUHD1E103                      EEUHD1E103                      C5, C6, C7, C8, C9, C10                                                                                                                                               
4   100n                            C-EUC0603                       C0603                           C12, C14, C16, C18                                                                                         CAPACITOR, European symbol           73         C          
2   100u/25V                        CPOL-EU153CLV-0810              153CLV-0810                     C13, C17                                                                                                   POLARIZED CAPACITOR, European symbol 4          C          
4   10n/1kV                         C-EUC1808                       C1808                           C1, C2, C3, C4                                                                                             CAPACITOR, European symbol           0          C          
2   113-314-04                      113-314-04                      113-314-04                      LED_+12V_OK, LED_-12V_OK                                                                                                                                              
2   22u/25V                         CPOL-EU153CLV-0505              153CLV-0505                     C11, C15                                                                                                   POLARIZED CAPACITOR, European symbol 3          C          
2   360/2W                          R-EU_R2010                      R2010                           R1, R3                                                                                                     RESISTOR, European symbol            3          R          
1   60807-011                       60807-011                       60807-011                       PCB_BRACKET                                                                                                                                                           
2   680                             R-EU_R0603                      R0603                           R2, R4                                                                                                     RESISTOR, European symbol            70         R          
2   FK 237 SA 220 O                 FK_237_SA_220_O                 FK_237_SA_220_O                 HS1, HS2                                                                                                                                                              
1   FL 24/12                        FL_24-12                        FL_24-12                        TF1                                                                                                                                                                   
1   GBJ610                          GBJ610                          GBJ610                          BR1                                                                                                                                                                   
1   LM1085IT-12                     LM1085IT-12                     LM1085IT-12                     IC1                                                                                                                                                                   
1   LM2990T-12                      LM2990T-12                      LM2990T-12                      IC2                                                                                                                                                                   
2   NB-PTCO-160                     NB-PTCO-160                     NB-PTCO-160                     TS1, TS2                                                                                                                                                              
2   RSPRO-SPDT-SLIDE-SWITCH-7347334 RSPRO-SPDT-SLIDE-SWITCH-7347334 RSPRO-SPDT-SLIDE-SWITCH-7347334 SWITCH_+12V, SWITCH_-12V

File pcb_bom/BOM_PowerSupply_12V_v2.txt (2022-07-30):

Qty Value           Device                          Package                         Parts                              Description                          POPULARITY SPICEPREFIX
4                   RSPRO-1MM-TERMINAL-POST-2622034 RSPRO-1MM-TERMINAL-POST-2622034 TP_+12V, TP_-12V, TP_GND1, TP_GND2                                                            
2   0031.8201       0031.8201                       0031.8201                       FUSE_+12V, FUSE_-12V                                                                          
1   09031326921     09031326921                     09031326921                     CON_BACKPLANE                                                                                 
4   100n            C-EUC0603                       C0603                           C3, C5, C8, C10                    CAPACITOR, European symbol           73         C          
2   100u/25V        CPOL-EU153CLV-0810              153CLV-0810                     C4, C9                             POLARIZED CAPACITOR, European symbol 4          C          
2   113-314-04      113-314-04                      113-314-04                      LED_+12V_OK, LED_-12V_OK                                                                      
4   22u/25V         CPOL-EU153CLV-0505              153CLV-0505                     C1, C2, C6, C7                     POLARIZED CAPACITOR, European symbol 3          C          
1   60807-011       60807-011                       60807-011                       PCB_BRACKET                                                                                   
2   680             R-EU_R0603                      R0603                           R1, R2                             RESISTOR, European symbol            70         R          
2   FK 237 SA 220 O FK_237_SA_220_O                 FK_237_SA_220_O                 HS1, HS2                                                                                      
1   L7812CV         L7812CV                         L7812CV                         IC1                                                                                           
1   L7912CV         L7912CV                         L7912CV                         IC2                                                                                           
2   TMLM_20115      TMLM_201XX                      TMLM_201XX                      PS1, PS2                                                                                      
2   VLS6045AF-101M  VLS6045AF-101M                  VLS6045AF-101M                  L1, L2

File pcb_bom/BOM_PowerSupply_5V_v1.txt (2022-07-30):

Qty Value                           Device                          Package                         Parts                                                                                                                           Description                          POPULARITY SPICEPREFIX
10                                  RSPRO-1MM-TERMINAL-POST-2622034 RSPRO-1MM-TERMINAL-POST-2622034 TP_+5V, TP_BITE_PS_+5V_CURRENT, TP_GND1, TP_GND2, TP_GND3, TP_GND4, TP_HALL_SENSOR_VIOUT, TP_RECT_OUT, TP_TF_SEC_A, TP_TF_SEC_B                                                            
1   0                               R-EU_R0603                      R0603                           R3                                                                                                                              RESISTOR, European symbol            70         R          
1   0031.8201                       0031.8201                       0031.8201                       FUSE_+5V                                                                                                                                                                                   
1   09031326921                     09031326921                     09031326921                     CON_BACKPLANE                                                                                                                                                                              
1   1000u/16V                       CPOL-EU153CLV-1010              153CLV-1010                     C16                                                                                                                             POLARIZED CAPACITOR, European symbol 0          C          
2   100k                            R-EU_R0603                      R0603                           R6, R7                                                                                                                          RESISTOR, European symbol            70         R          
6   100n                            C-EUC0603                       C0603                           C15, C17, C18, C20, C21, C22                                                                                                    CAPACITOR, European symbol           73         C          
4   10n/1kV                         C-EUC1808                       C1808                           C1, C2, C3, C4                                                                                                                  CAPACITOR, European symbol           0          C          
1   10u/16V                         CPOL-EU153CLV-0405              153CLV-0405                     C14                                                                                                                             POLARIZED CAPACITOR, European symbol 0          C          
1   113-314-04                      113-314-04                      113-314-04                      LED_+5V_OK                                                                                                                                                                                 
1   150                             R-EU_R0603                      R0603                           R2                                                                                                                              RESISTOR, European symbol            70         R          
9   15000u/16V                      EEUHD1C153                      EEUHD1C153                      C5, C6, C7, C8, C9, C10, C11, C12, C13                                                                                                                                                     
1   27k                             R-EU_R0603                      R0603                           R8                                                                                                                              RESISTOR, European symbol            70         R          
1   2k                              R-EU_R0603                      R0603                           R5                                                                                                                              RESISTOR, European symbol            70         R          
1   3k                              R-EU_R0603                      R0603                           R4                                                                                                                              RESISTOR, European symbol            70         R          
1   470n                            C-EUC0603                       C0603                           C19                                                                                                                             CAPACITOR, European symbol           73         C          
1   60807-011                       60807-011                       60807-011                       PCB_BRACKET                                                                                                                                                                                
1   82/2W                           R-EU_R2010                      R2010                           R1                                                                                                                              RESISTOR, European symbol            3          R          
1   ACS712ELCTR-05B-T               ACS712ELCTR-05B-T               ACS712ELCTR-05B-T               IC2                                                                                                                                                                                        
1   FK 237 SA 220 O                 FK_237_SA_220_O                 FK_237_SA_220_O                 HS1                                                                                                                                                                                        
1   FL 24/6                         FL_24-6                         FL_24-6                         TF1                                                                                                                                                                                        
1   GBJ610                          GBJ610                          GBJ610                          BR1                                                                                                                                                                                        
1   MCP6L1T-E/OT                    MCP6L1T-E/OT                    MCP6L1T-E/OT                    OP1                                                                                                                                                                                        
1   MIC29300-5.0WT                  MIC29300-5.0WT                  MIC29300-5.0WT                  IC1                                                                                                                                                                                        
2   NB-PTCO-160                     NB-PTCO-160                     NB-PTCO-160                     TS1, TS2                                                                                                                                                                                   
1   RSPRO-SPDT-SLIDE-SWITCH-7347334 RSPRO-SPDT-SLIDE-SWITCH-7347334 RSPRO-SPDT-SLIDE-SWITCH-7347334 SWITCH_+5V

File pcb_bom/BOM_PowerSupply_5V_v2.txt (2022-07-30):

Qty Value       Device                          Package                         Parts            Description                          POPULARITY SPICEPREFIX
2               RSPRO-1MM-TERMINAL-POST-2622034 RSPRO-1MM-TERMINAL-POST-2622034 TP_GND1, TP_GND2                                                            
1   0031.8201   0031.8201                       0031.8201                       FUSE_+5V                                                                    
1   09031326921 09031326921                     09031326921                     CON_BACKPLANE                                                               
1   100n        C-EUC0603                       C0603                           C2               CAPACITOR, European symbol           73         C          
1   113-314-04  113-314-04                      113-314-04                      LED_+5V_OK                                                                  
1   150         R-EU_R0603                      R0603                           R1               RESISTOR, European symbol            70         R          
1   47u/16V     CPOL-EU153CLV-0505              153CLV-0505                     C1               POLARIZED CAPACITOR, European symbol 3          C          
1   60807-011   60807-011                       60807-011                       PCB_BRACKET                                                                 
1   TMLM_20105  TMLM_201XX                      TMLM_201XX                      PS1

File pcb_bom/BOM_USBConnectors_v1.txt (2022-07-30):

Qty Value          Device                Package               Parts                           Description                POPULARITY SPICEPREFIX
2   1.5k           R-EU_R0603            R0603                 R1, R2                          RESISTOR, European symbol  70         R          
5   100n           C-EUC0603             C0603                 C2, C4, C5, C6, C7              CAPACITOR, European symbol 73         C          
1   10n            C-EUC0603             C0603                 C1                              CAPACITOR, European symbol 73         C          
1   113-305-04     113-305-04            113-305-04            LED_USB_DEBUG_TX                                                                 
1   113-311-04     113-311-04            113-311-04            LED_USB_DEBUG_RX                                                                 
1   4.7u           C-EUC0603             C0603                 C3                              CAPACITOR, European symbol 73         C          
2   500 mA         LITTELFUSE_466_SERIES LITTELFUSE_466_SERIES F1, F2                                                                           
1   60807-181_A    60807-181_A           60807-181_A           PCB_BRACKET1                                                                     
1   60807-181_B    60807-181_B           60807-181_B           PCB_BRACKET2                                                                     
2   61729-1011BLF  61729-1011BLF         61729-1011BLF         CON_USB-B_DATA, CON_USB-B_DEBUG                                                  
1   ADUM1201ARZ    ADUM1201              SO8                   IC2                                                                              
1   FT232RL        FT232RL               FT232RL               IC1                                                                              
1   TST-105-01-T-D TST-105-01-T-D        TST-105-01-T-D        CON_BACKPLANE

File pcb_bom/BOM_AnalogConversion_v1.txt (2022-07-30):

Qty Value                Device                          Package                         Parts                                                                                                                                                                                                                                                 Description                          POPULARITY SPICEPREFIX
4                        LEDCHIP-LED0603                 CHIP-LED0603                    LED_+3.3V, LED_+5V_ADC, LED_+5V_FRONTEND, LED_-5V_FRONTEND                                                                                                                                                                                            LED                                  26                    
17                       RSPRO-1MM-TERMINAL-POST-2622034 RSPRO-1MM-TERMINAL-POST-2622034 TP_ADC_NRESET, TP_GND1, TP_GND2, TP_GND3, TP_GND4, TP_I2C_NINT, TP_I2C_SCL, TP_I2C_SDA, TP_RD_NCS, TP_RD_NRESET, TP_SPI_CONFIG_ADC_NCS, TP_SPI_CONFIG_CLK, TP_SPI_CONFIG_MISO, TP_SPI_CONFIG_MOSI, TP_SPI_DATA_CLK, TP_SPI_DATA_MOSI, TP_SPI_DATA_NCS                                                            
3                        SJ2W                            SJ_2                            SJ1, SJ2, SJ3                                                                                                                                                                                                                                         SMD solder JUMPER                    7                     
1   09031326921          09031326921                     09031326921                     CON_BACKPLANE                                                                                                                                                                                                                                                                                                    
3   1.8k                 R-EU_R0603                      R0603                           R2, R23, R24                                                                                                                                                                                                                                          RESISTOR, European symbol            70         R          
6   100                  R-EU_R0603                      R0603                           R25, R26, R27, R28, R29, R30                                                                                                                                                                                                                          RESISTOR, European symbol            70         R          
1   1000u/16V            CPOL-EU153CLV-1010              153CLV-1010                     C1                                                                                                                                                                                                                                                    POLARIZED CAPACITOR, European symbol 0          C          
26  100n                 C-EUC0603                       C0603                           C9, C10, C12, C14, C16, C18, C20, C22, C24, C26, C28, C30, C31, C32, C34, C35, C40, C42, C44, C57, C58, C59, C60, C63, C64, C66                                                                                                                       CAPACITOR, European symbol           73         C          
3   100u                 VLS6045AF-101M                  VLS6045AF-101M                  L1, L2, L3                                                                                                                                                                                                                                                                                                       
2   100u/25V             CPOL-EU153CLV-0810              153CLV-0810                     C2, C3                                                                                                                                                                                                                                                POLARIZED CAPACITOR, European symbol 4          C          
2   10k                  3296W                           3296W                           POT1, POT2                                                                                                                                                                                                                                                                                                       
1   10k                  R-EU_R0603                      R0603                           R3                                                                                                                                                                                                                                                    RESISTOR, European symbol            70         R          
1   10u                  C-EUC0603                       C0603                           C21                                                                                                                                                                                                                                                   CAPACITOR, European symbol           73         C          
7   10u                  CPOL-EUCT3216                   CT3216                          C4, C6, C7, C46, C47, C49, C50                                                                                                                                                                                                                        POLARIZED CAPACITOR, European symbol 1          C          
1   10u/16V              C-EUC0805                       C0805                           C29                                                                                                                                                                                                                                                   CAPACITOR, European symbol           88         C          
2   113-305-04           113-305-04                      113-305-04                      LED_SHORT_CH1, LED_SHORT_CH2                                                                                                                                                                                                                                                                                     
2   150                  R-EU_R0603                      R0603                           R31, R32                                                                                                                                                                                                                                              RESISTOR, European symbol            70         R          
2   1k                   R-EU_R0603                      R0603                           R4, R5                                                                                                                                                                                                                                                RESISTOR, European symbol            70         R          
3   1n                   C-EUC0603                       C0603                           C33, C61, C62                                                                                                                                                                                                                                         CAPACITOR, European symbol           73         C          
10  1u                   C-EUC0603                       C0603                           C11, C13, C15, C17, C19, C23, C25, C41, C43, C65                                                                                                                                                                                                      CAPACITOR, European symbol           73         C          
1   2                    R-EU_R0603                      R0603                           R9                                                                                                                                                                                                                                                    RESISTOR, European symbol            70         R          
4   220p                 C-EUC0603                       C0603                           C53, C54, C55, C56                                                                                                                                                                                                                                    CAPACITOR, European symbol           73         C          
1   22u                  C-EUC1206                       C1206                           C27                                                                                                                                                                                                                                                   CAPACITOR, European symbol           54         C          
4   22u                  CPOL-EUCT6032                   CT6032                          C5, C8, C48, C51                                                                                                                                                                                                                                      POLARIZED CAPACITOR, European symbol 2          C          
2   2337019-1            2337019-1                       2337019-1                       CON_INT_CH1, CON_INT_CH2                                                                                                                                                                                                                                                                                         
1   43.2k                R-EU_R0603                      R0603                           R7                                                                                                                                                                                                                                                    RESISTOR, European symbol            70         R          
1   47                   R-EU_R0603                      R0603                           R14                                                                                                                                                                                                                                                   RESISTOR, European symbol            70         R          
8   470                  R-EU_R0603                      R0603                           R15, R16, R17, R18, R19, R20, R21, R22                                                                                                                                                                                                                RESISTOR, European symbol            70         R          
1   499                  R-EU_R0603                      R0603                           R8                                                                                                                                                                                                                                                    RESISTOR, European symbol            70         R          
2   5-1462037-8          5-1462037-8                     5-1462037-8                     RELAY1, RELAY2                                                                                                                                                                                                                                                                                                   
1   510                  R-EU_R0603                      R0603                           R6                                                                                                                                                                                                                                                    RESISTOR, European symbol            70         R          
1   60807-011            60807-011                       60807-011                       PCB_BRACKET                                                                                                                                                                                                                                                                                                      
1   750                  R-EU_R0603                      R0603                           R1                                                                                                                                                                                                                                                    RESISTOR, European symbol            70         R          
4   82                   R-EU_R0603                      R0603                           R10, R11, R12, R13                                                                                                                                                                                                                                    RESISTOR, European symbol            70         R          
4   82p                  C-EUC0603                       C0603                           C36, C37, C38, C39                                                                                                                                                                                                                                    CAPACITOR, European symbol           73         C          
1   AD7768-4BSTZ         AD7768-4BSTZ                    AD7768-4BSTZ                    ADC                                                                                                                                                                                                                                                                                                              
1   ADA4841-1YRJZ        ADA4841-1YRJZ                   ADA4841-1YRJZ                   IC4                                                                                                                                                                                                                                                                                                              
2   ADA4945-1ACPZ-R7     ADA4945-1ACPZ-R7                ADA4945-1ACPZ-R7                IC5, IC6                                                                                                                                                                                                                                                                                                         
1   ADR444BRZ            ADR444BRZ                       ADR444BRZ                       IC3                                                                                                                                                                                                                                                                                                              
2   DELOCK_65848         DELOCK_65848                    DELOCK_65848                    CON_EXT_CH1, CON_EXT_CH2                                                                                                                                                                                                                                                                                         
1   L79L05ACUTR          L79L05ACUTR                     L79L05ACUTR                     IC8                                                                                                                                                                                                                                                                                                              
1   LM1117IMP-3.3        LM1117IMPX-3.3                  SOT223                          IC1                                                                                                                                                                                                                                                                                                              
2   LM1117MP-5.0         LM1117MPX-5.0                   SOT223                          IC2, IC7                                                                                                                                                                                                                                                                                                         
1   MAX4820EUP+          MAX4820EUP+                     MAX4820EUP+                     RD                                                                                                                                                                                                                                                                                                               
2   OP27GSZ              OP27D                           SO08                            IC9, IC10                                                                                                                                                                                                                                             OP AMP                               0                     
1   SG-210STF 32.7680ML3 SG-210STF-32.7680ML3            SG-210STF-32.7680ML3            OSC1                                                                                                                                                                                                                                                                                                             
1   TCA9534ADWR          TCA9534ADWR                     TCA9534ADWR                     IC11

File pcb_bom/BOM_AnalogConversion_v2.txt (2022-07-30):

Qty Value                Device                          Package                         Parts                                                                                                                                                                                                                                                                                                                          Description                          POPULARITY SPICEPREFIX
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

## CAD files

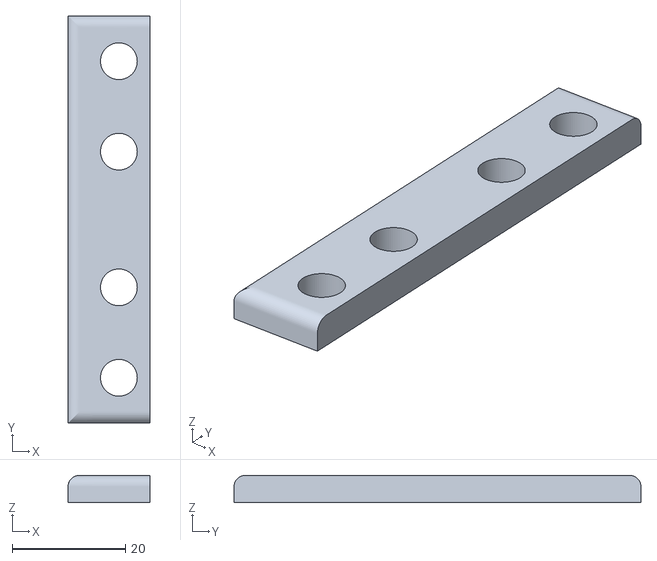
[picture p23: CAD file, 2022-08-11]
cad_complete/inventor/AnalogConversion_v3/Front_Panel/SMA_Spacer_AnalogConversion_v3.stl
14.5 x 72.0 x 4.80

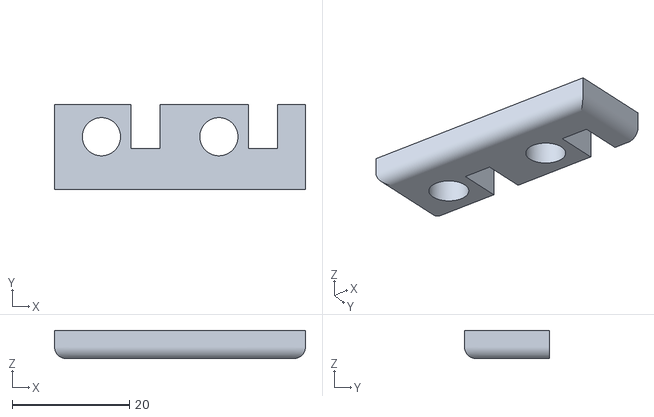
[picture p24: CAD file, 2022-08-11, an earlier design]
cad_complete/inventor/AnalogConversion_v2/Front_Panel/SMA_Spacer_AnalogConversion_v2.stl
42.8 x 14.5 x 4.80

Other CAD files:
cad_complete/inventor/AnalogConversion_v1/Front_Panel/20848664_AnalogConversion_v1.ipt
cad_complete/inventor/AnalogConversion_v1/PCB/09031326921.ipt
cad_complete/inventor/AnalogConversion_v1/PCB/113-305-04.ipt
cad_complete/inventor/AnalogConversion_v1/PCB/153CLV-0810.ipt
cad_complete/inventor/AnalogConversion_v1/PCB/153CLV-1010.ipt
cad_complete/inventor/AnalogConversion_v1/PCB/16-soldermask.ipt
cad_complete/inventor/AnalogConversion_v1/PCB/2337019-1.ipt
cad_complete/inventor/AnalogConversion_v1/PCB/3296W.ipt
cad_complete/inventor/AnalogConversion_v1/PCB/5-1462037-8.ipt
cad_complete/inventor/AnalogConversion_v1/PCB/60807-011.ipt
cad_complete/inventor/AnalogConversion_v1/PCB/AD7768-4BSTZ.ipt
cad_complete/inventor/AnalogConversion_v1/PCB/ADA4841-1YRJZ.ipt
cad_complete/inventor/AnalogConversion_v1/PCB/ADA4945-1ACPZ-R7.ipt
cad_complete/inventor/AnalogConversion_v1/PCB/ADR444BRZ.ipt
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

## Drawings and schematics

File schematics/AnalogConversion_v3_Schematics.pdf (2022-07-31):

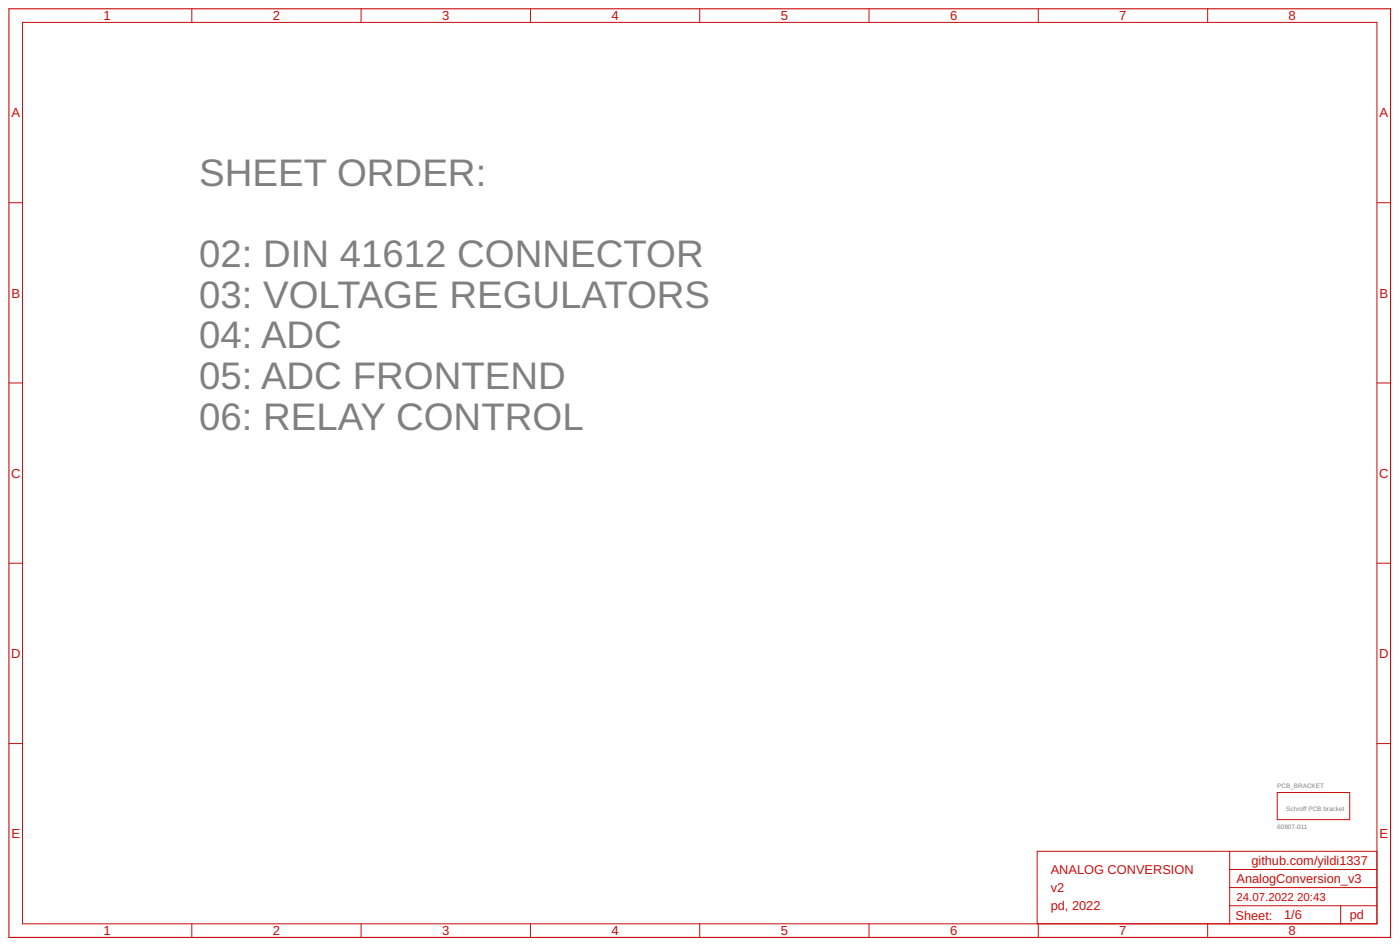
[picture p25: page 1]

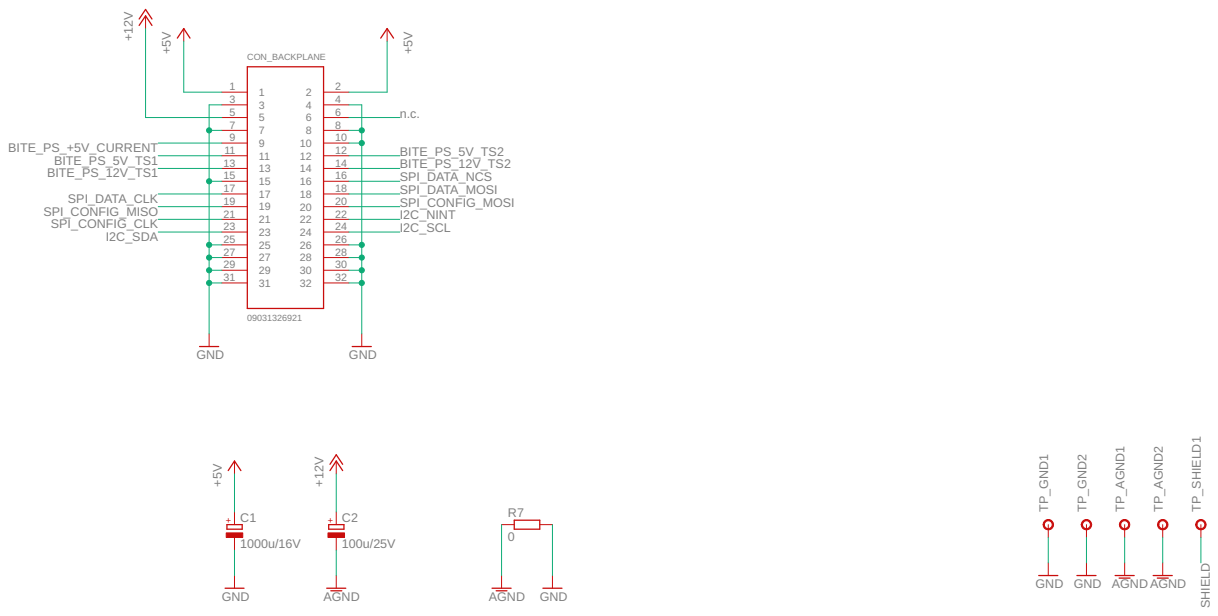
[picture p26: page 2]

27 | 28
29 | 30
31 | 32

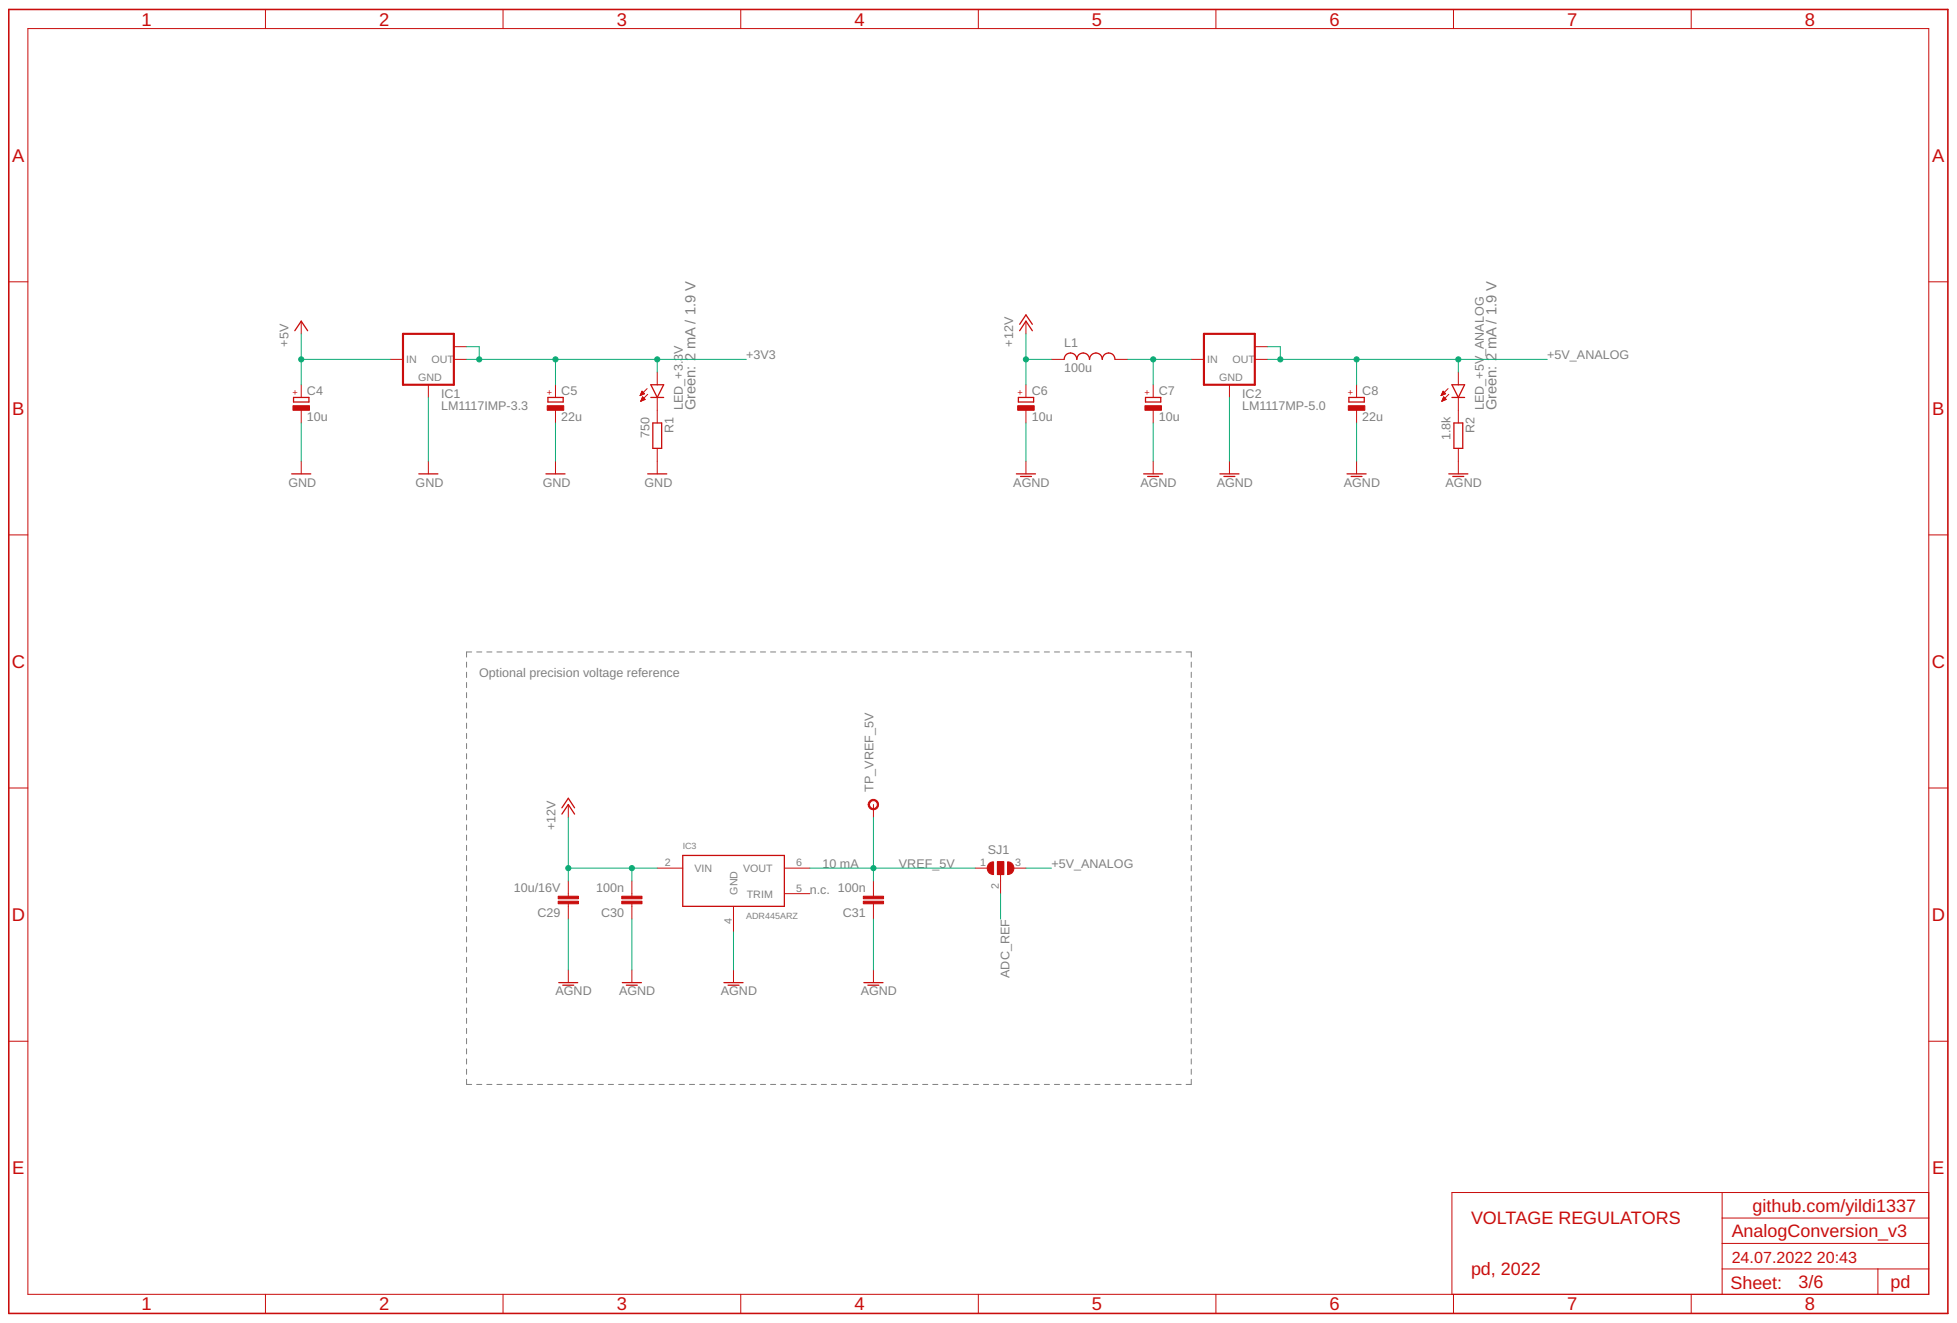
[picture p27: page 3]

Optional precision voltage reference

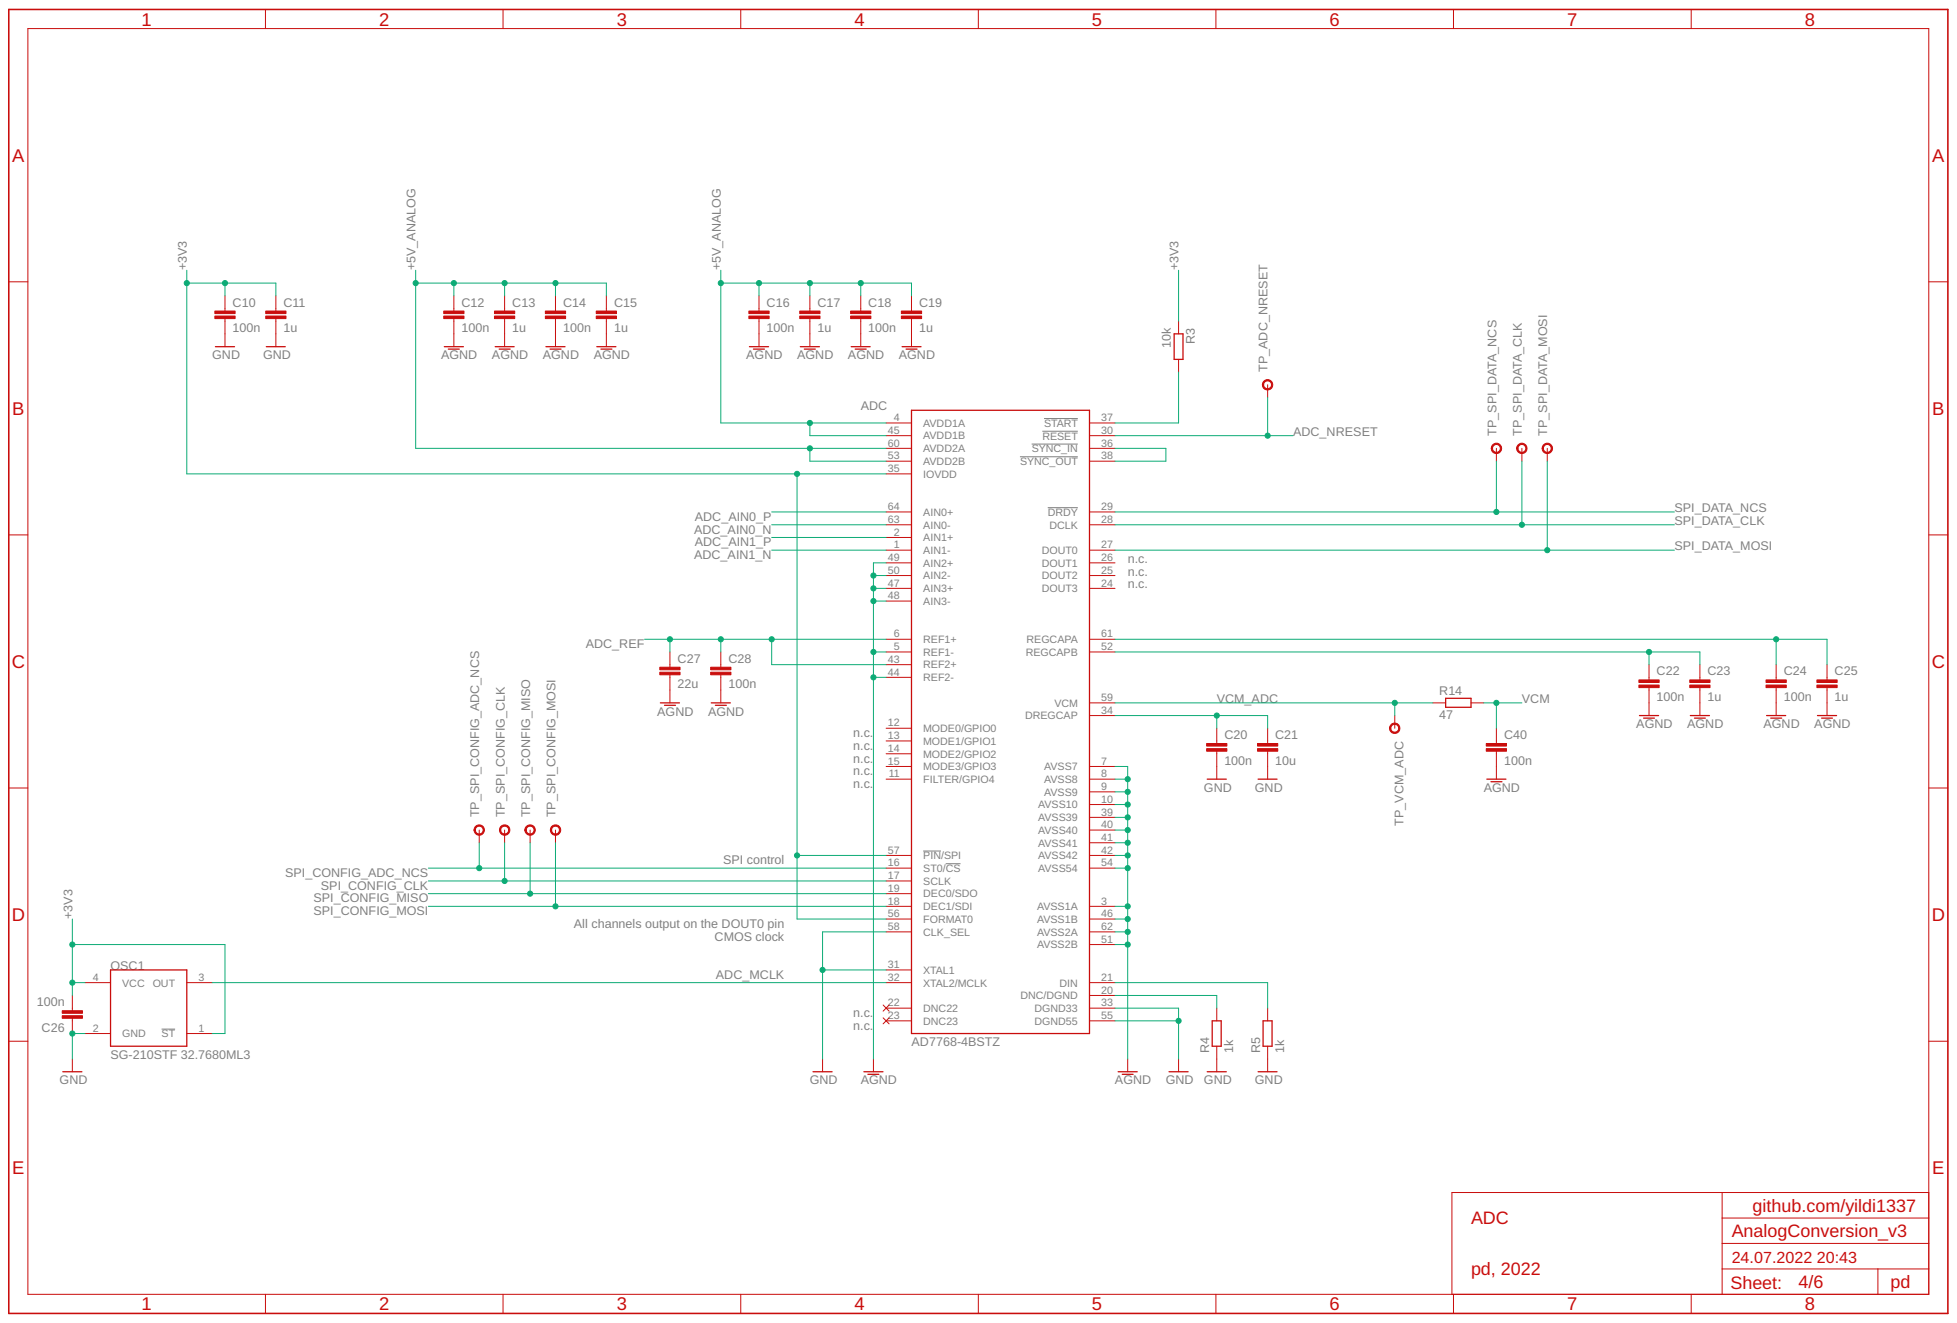
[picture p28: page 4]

n.c. n.c. n.c. n.c. n.c. SPI control

19 56 | DEC1/SDI 18 | 54

All channels output on the DOUT0 pin CMOS clock

3 ST | 21 DGND55 20

33 DNC/DGND

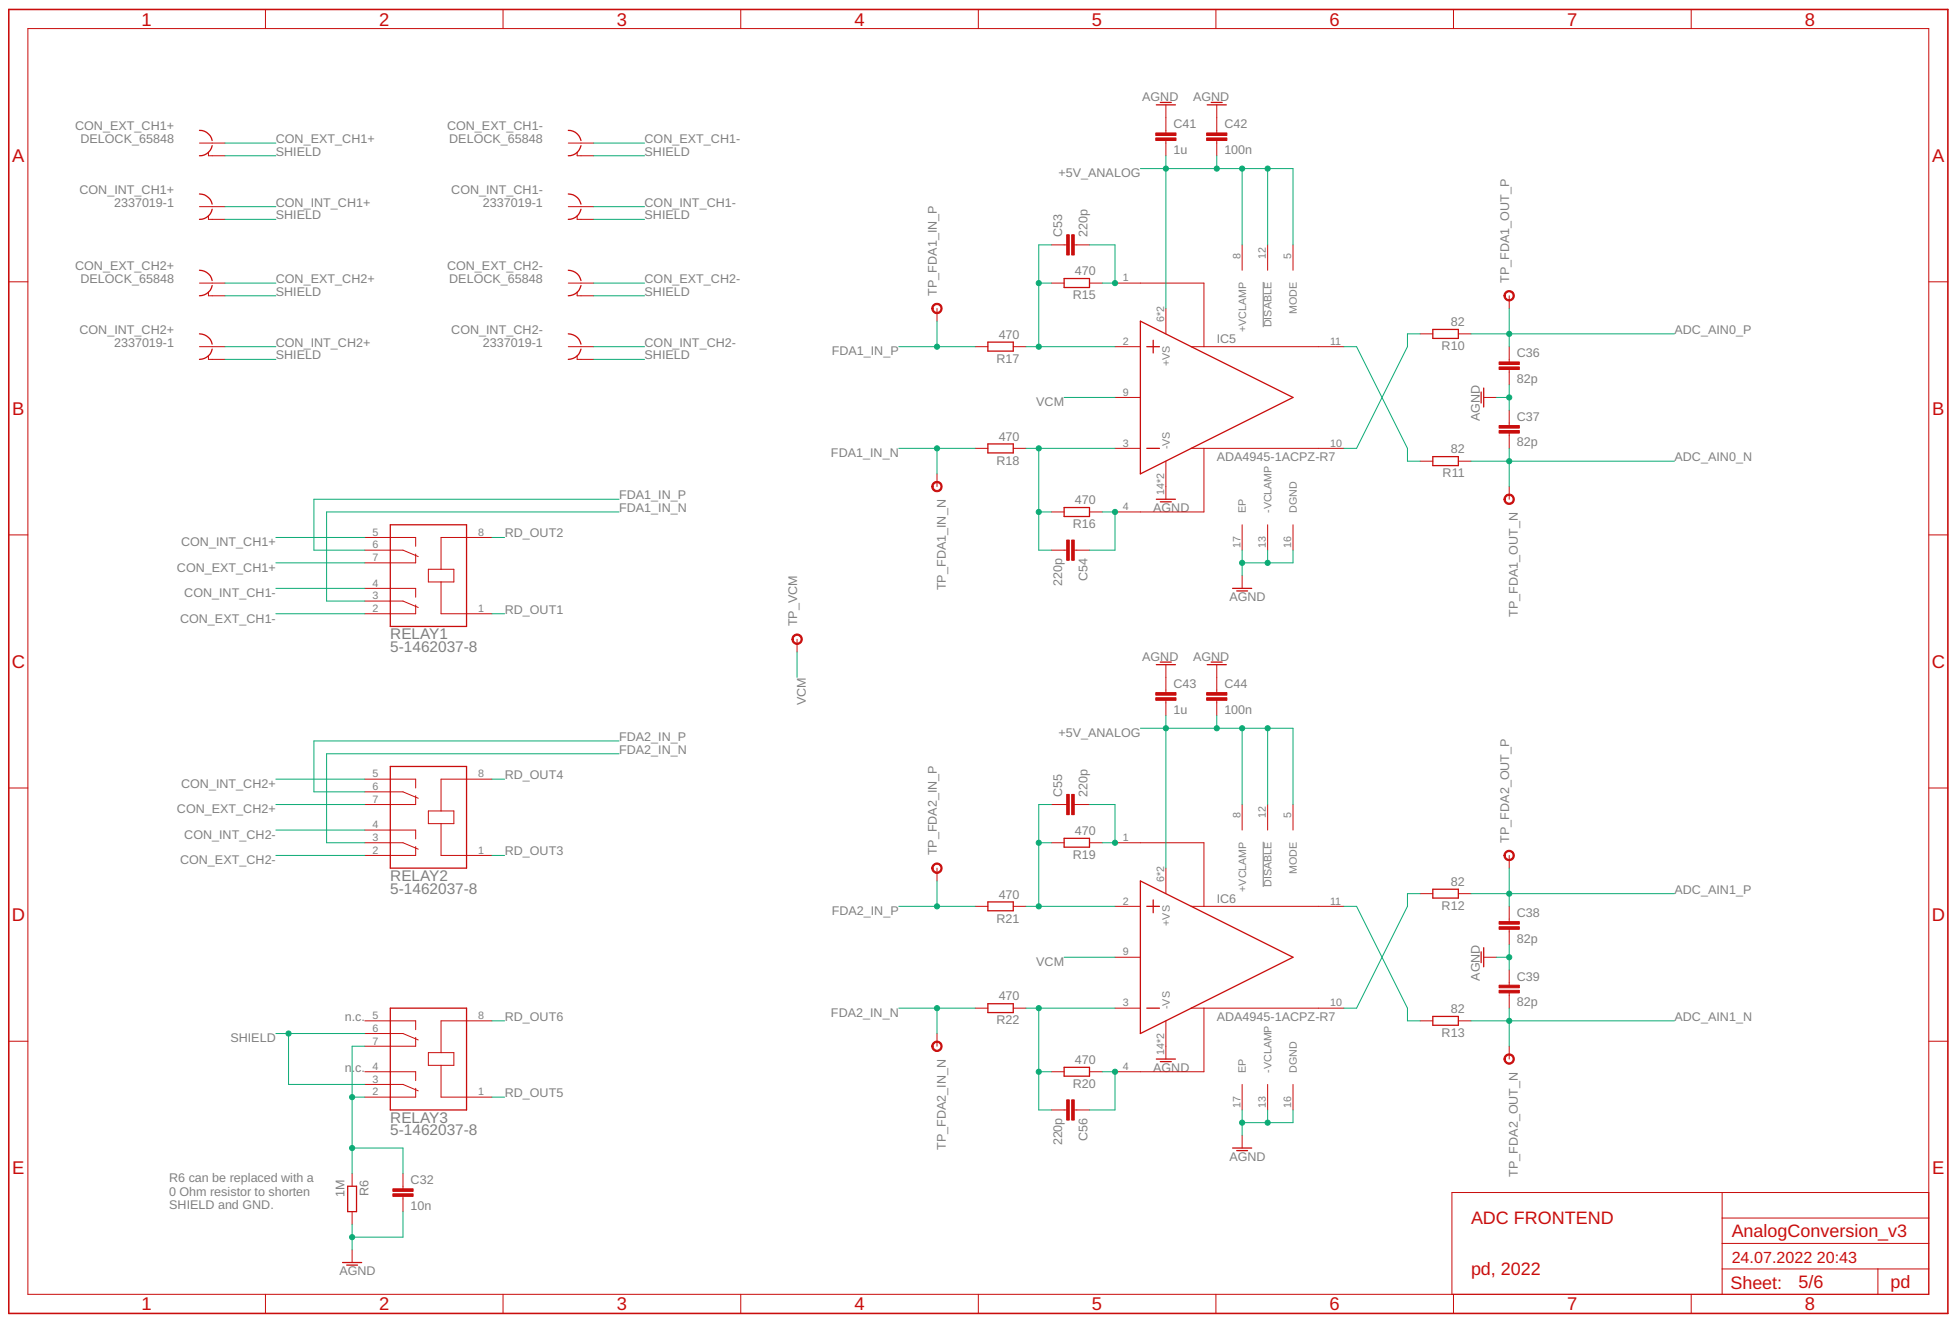
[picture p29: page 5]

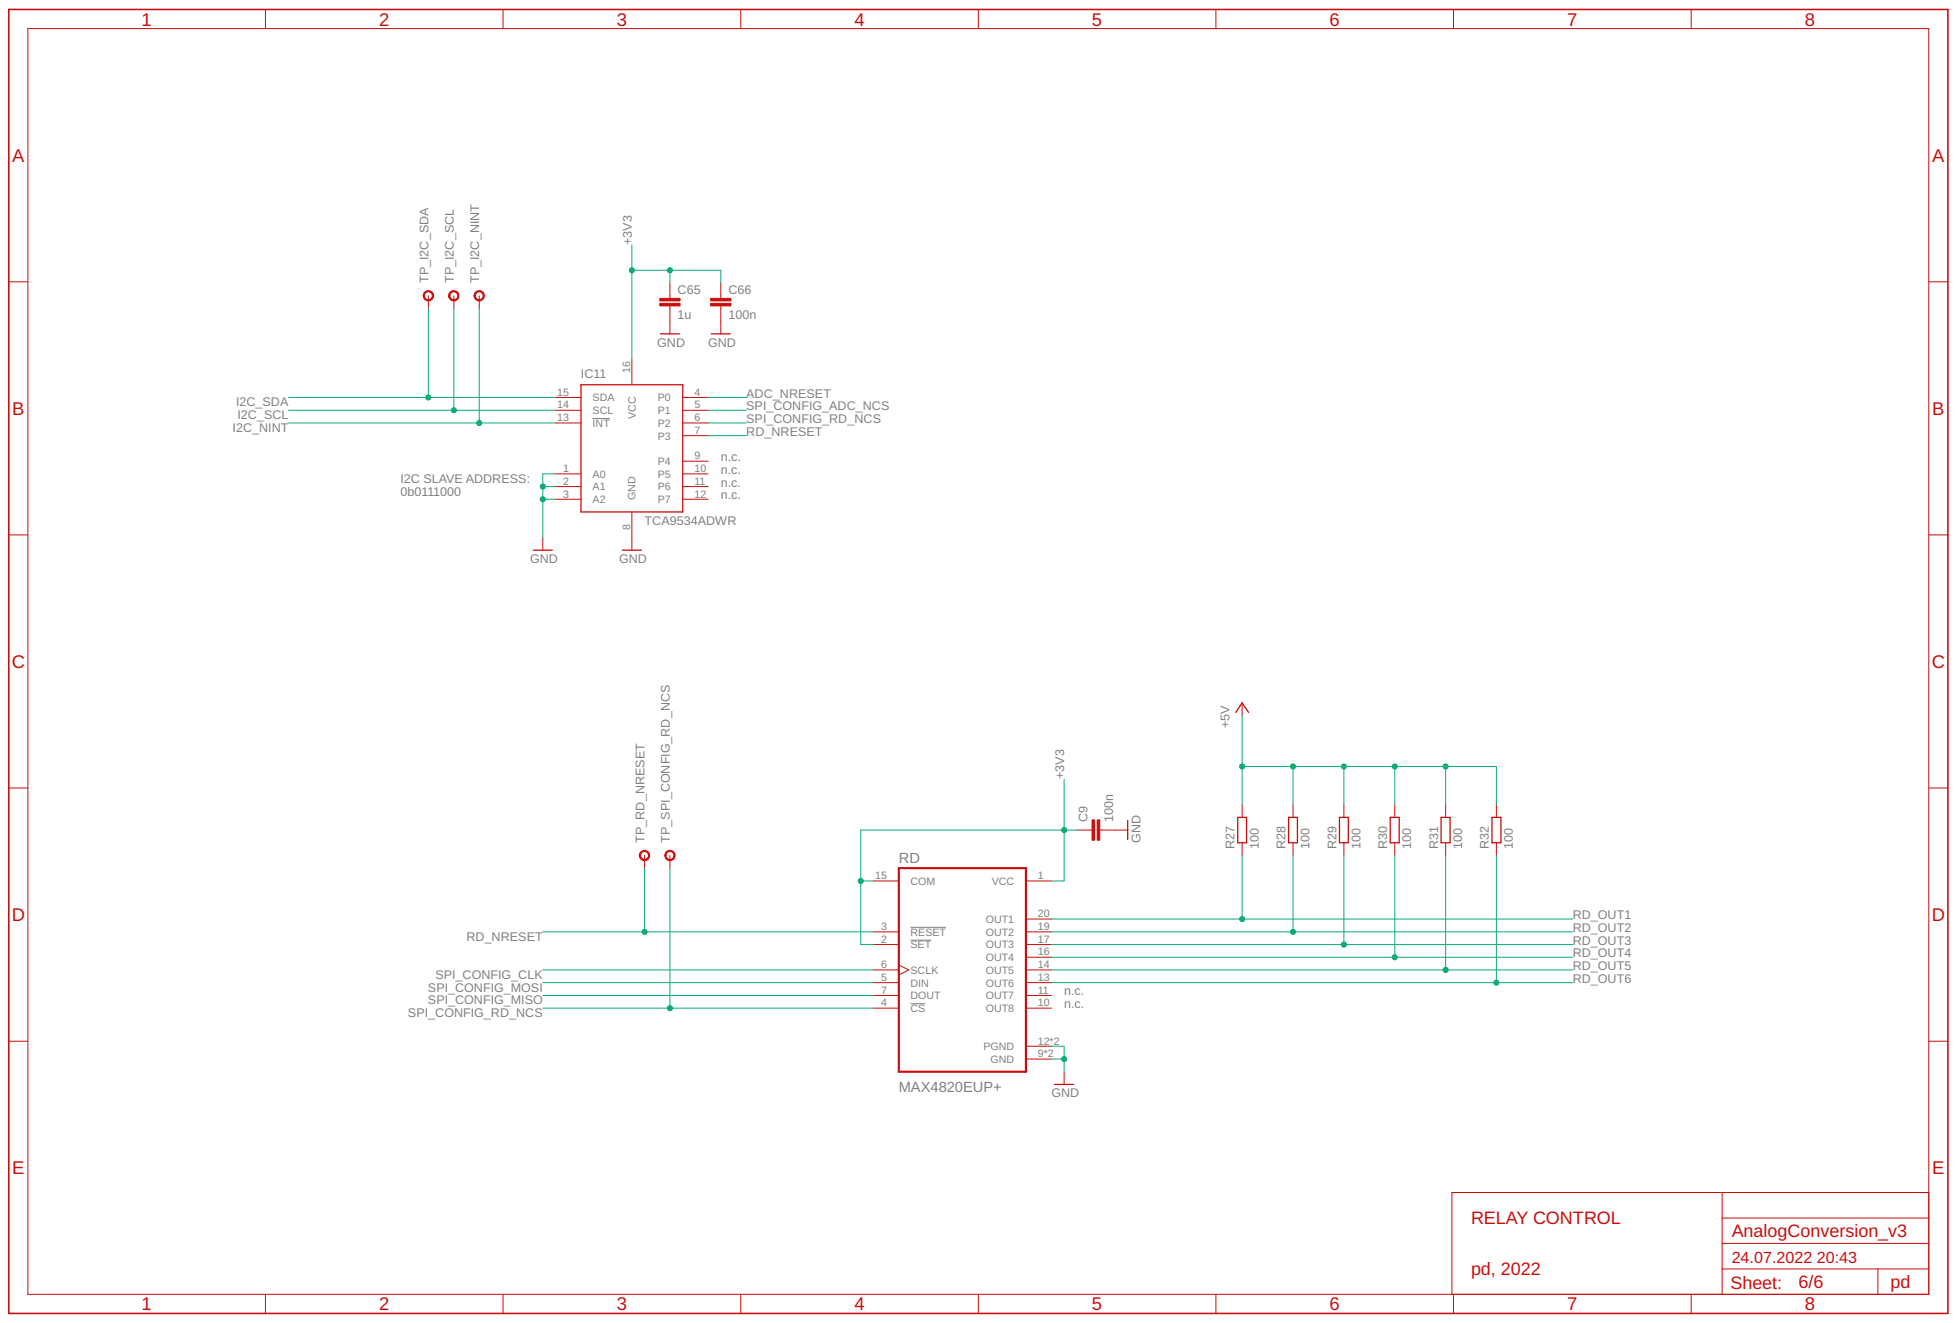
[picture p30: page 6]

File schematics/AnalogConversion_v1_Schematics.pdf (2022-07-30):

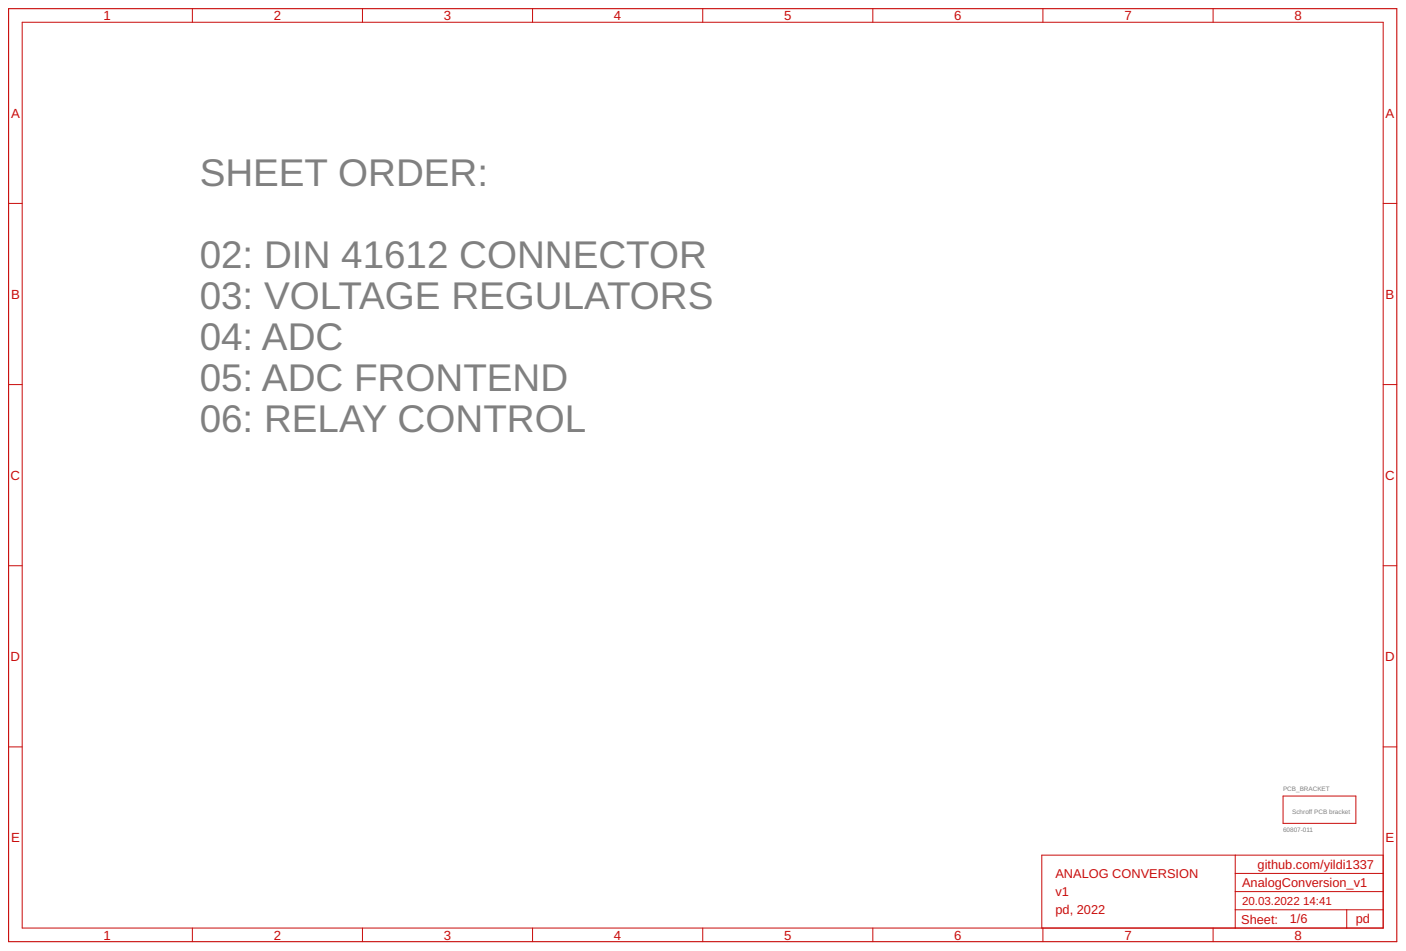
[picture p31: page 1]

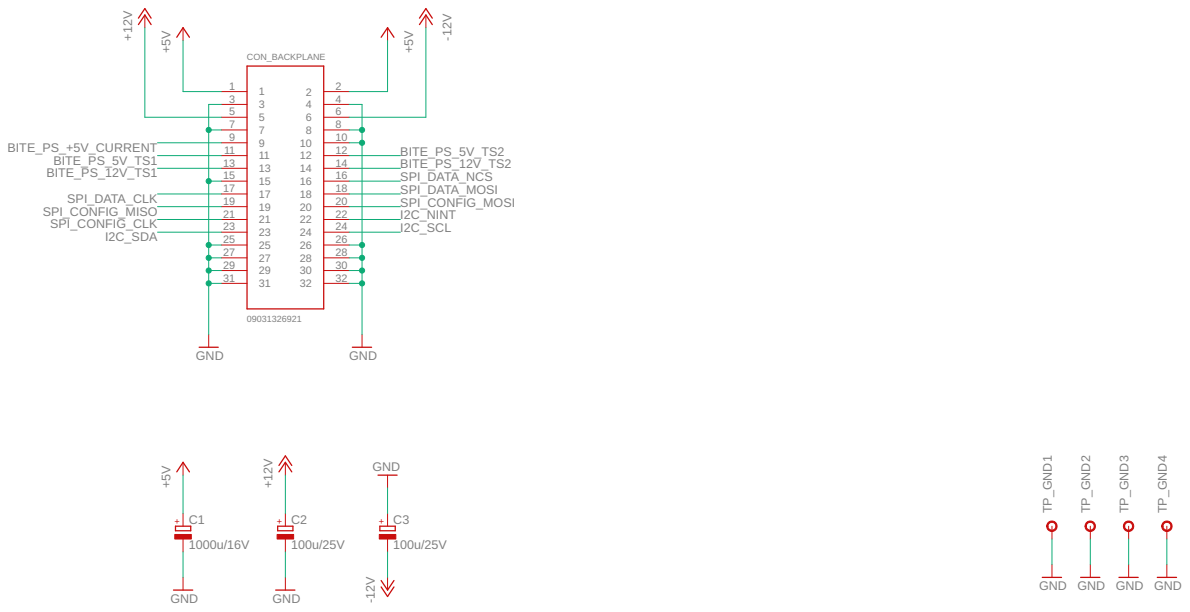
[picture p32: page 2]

9 11 13 15 | 10

27 | 28
29 | 30
31 | 32

GND GND

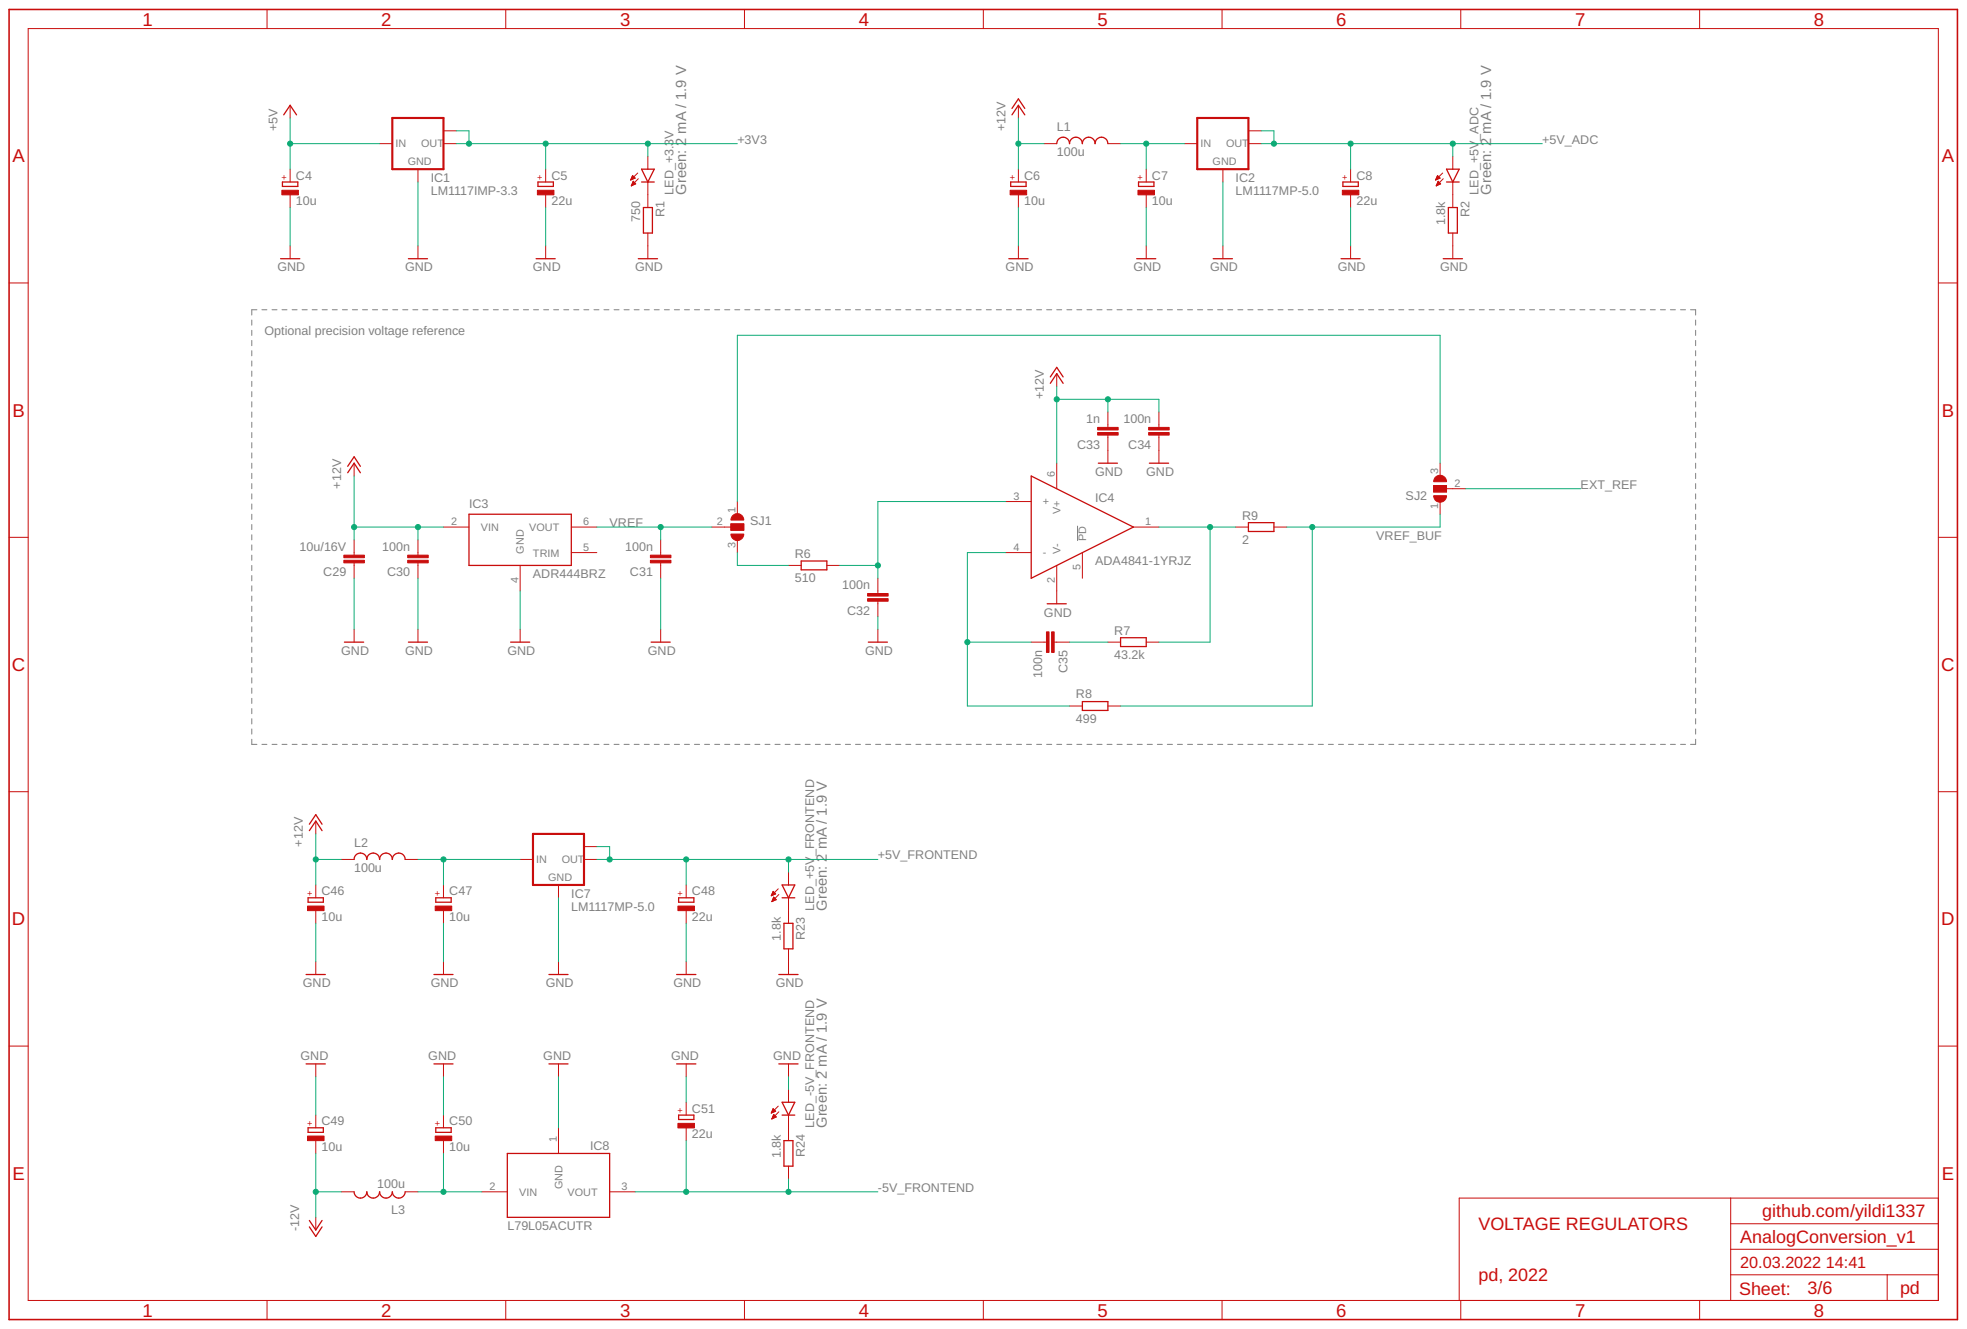
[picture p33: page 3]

Optional precision voltage reference

Green: 2 mA / 1.9 V

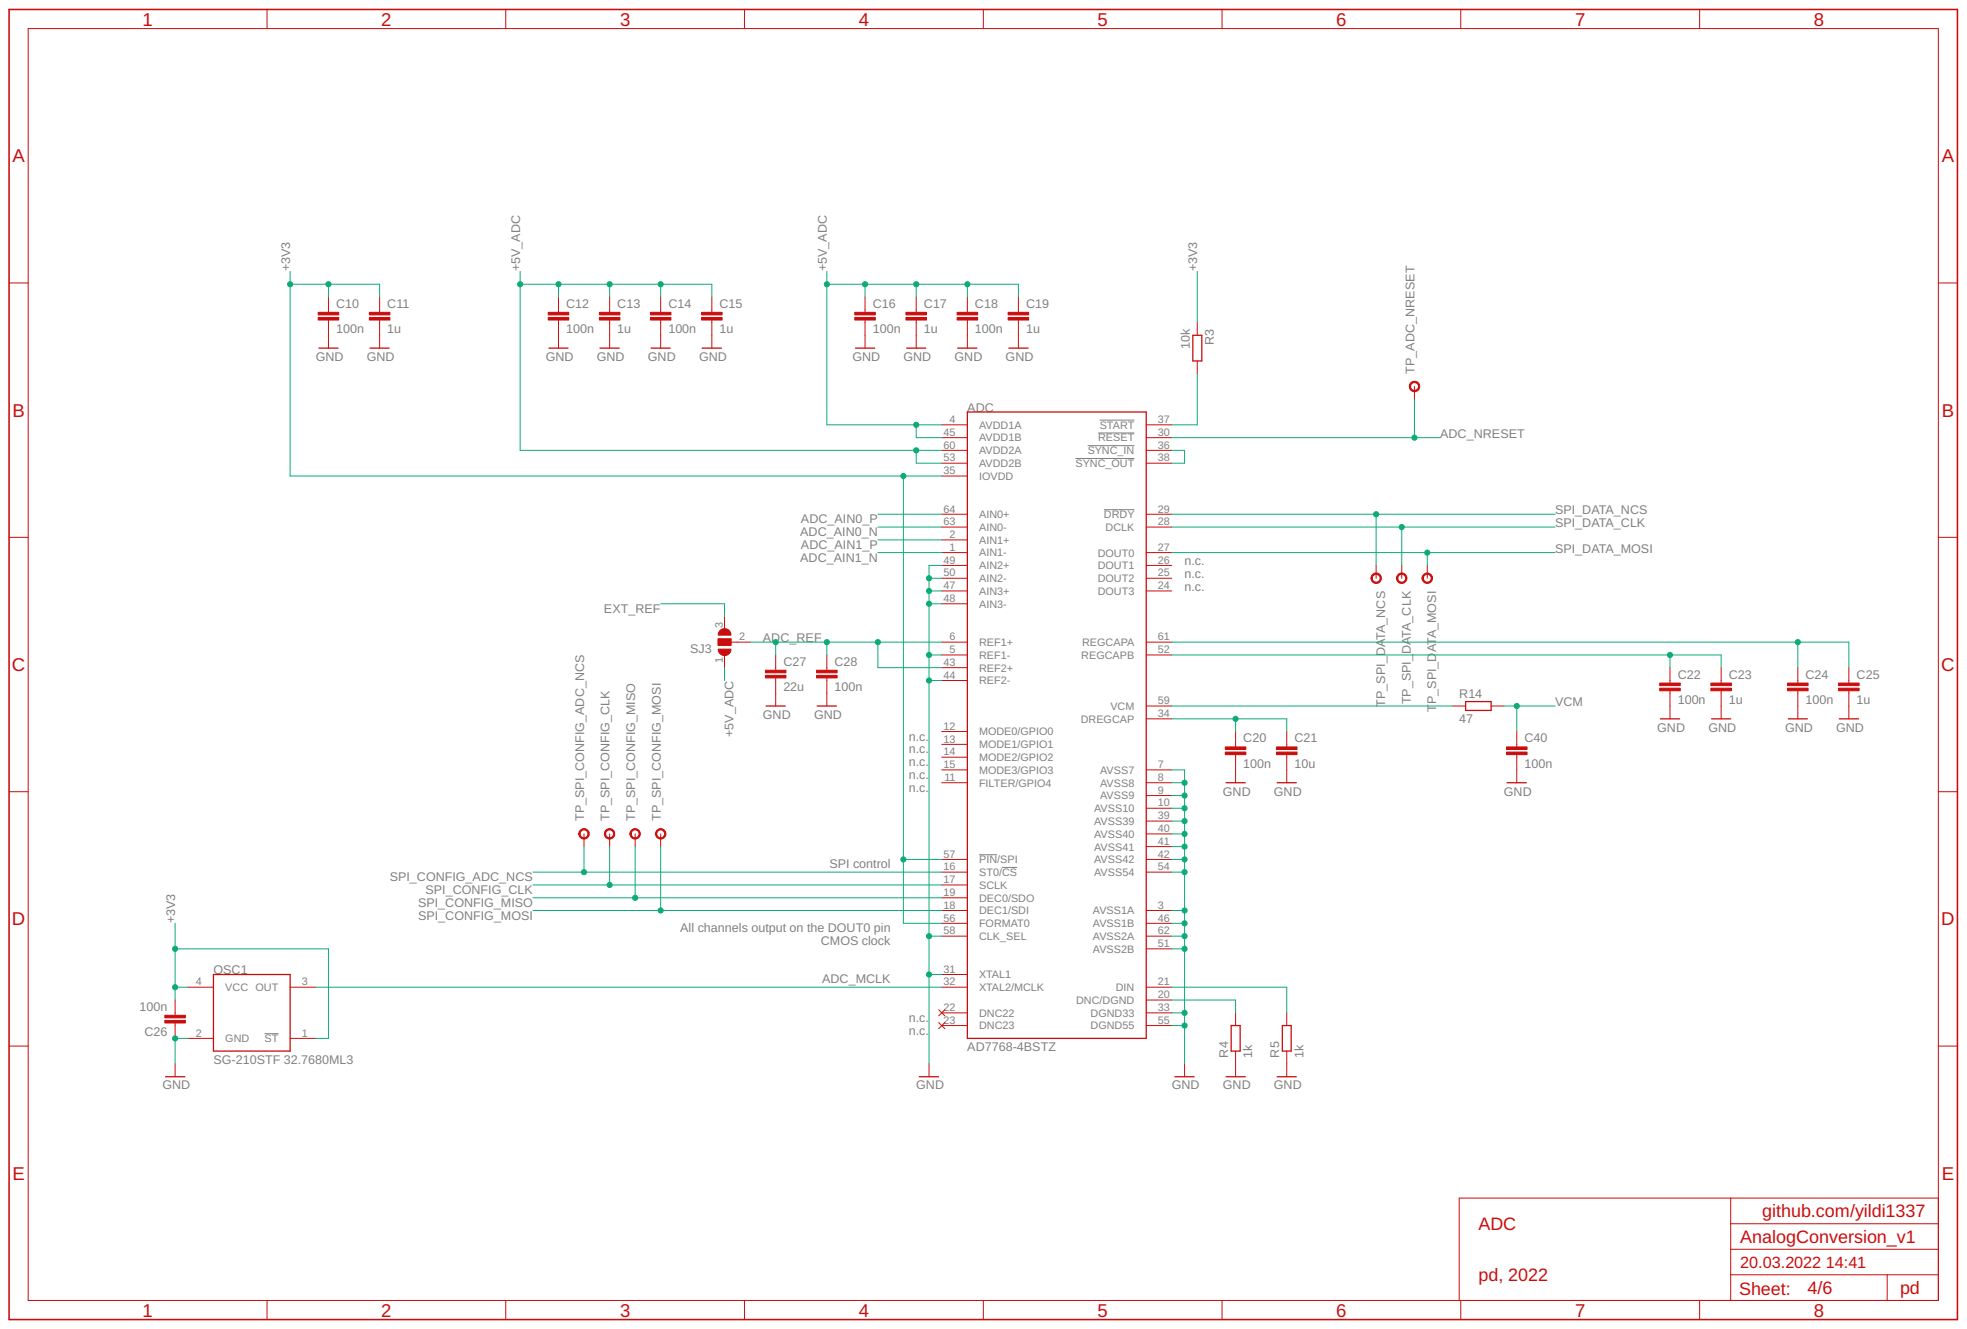
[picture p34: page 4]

19 56 | DEC1/SDI 18 | 42 AVSS54 54

All channels output on the DOUT0 pin CMOS clock

3 ST | 21 DGND55 20

33 DNC/DGND

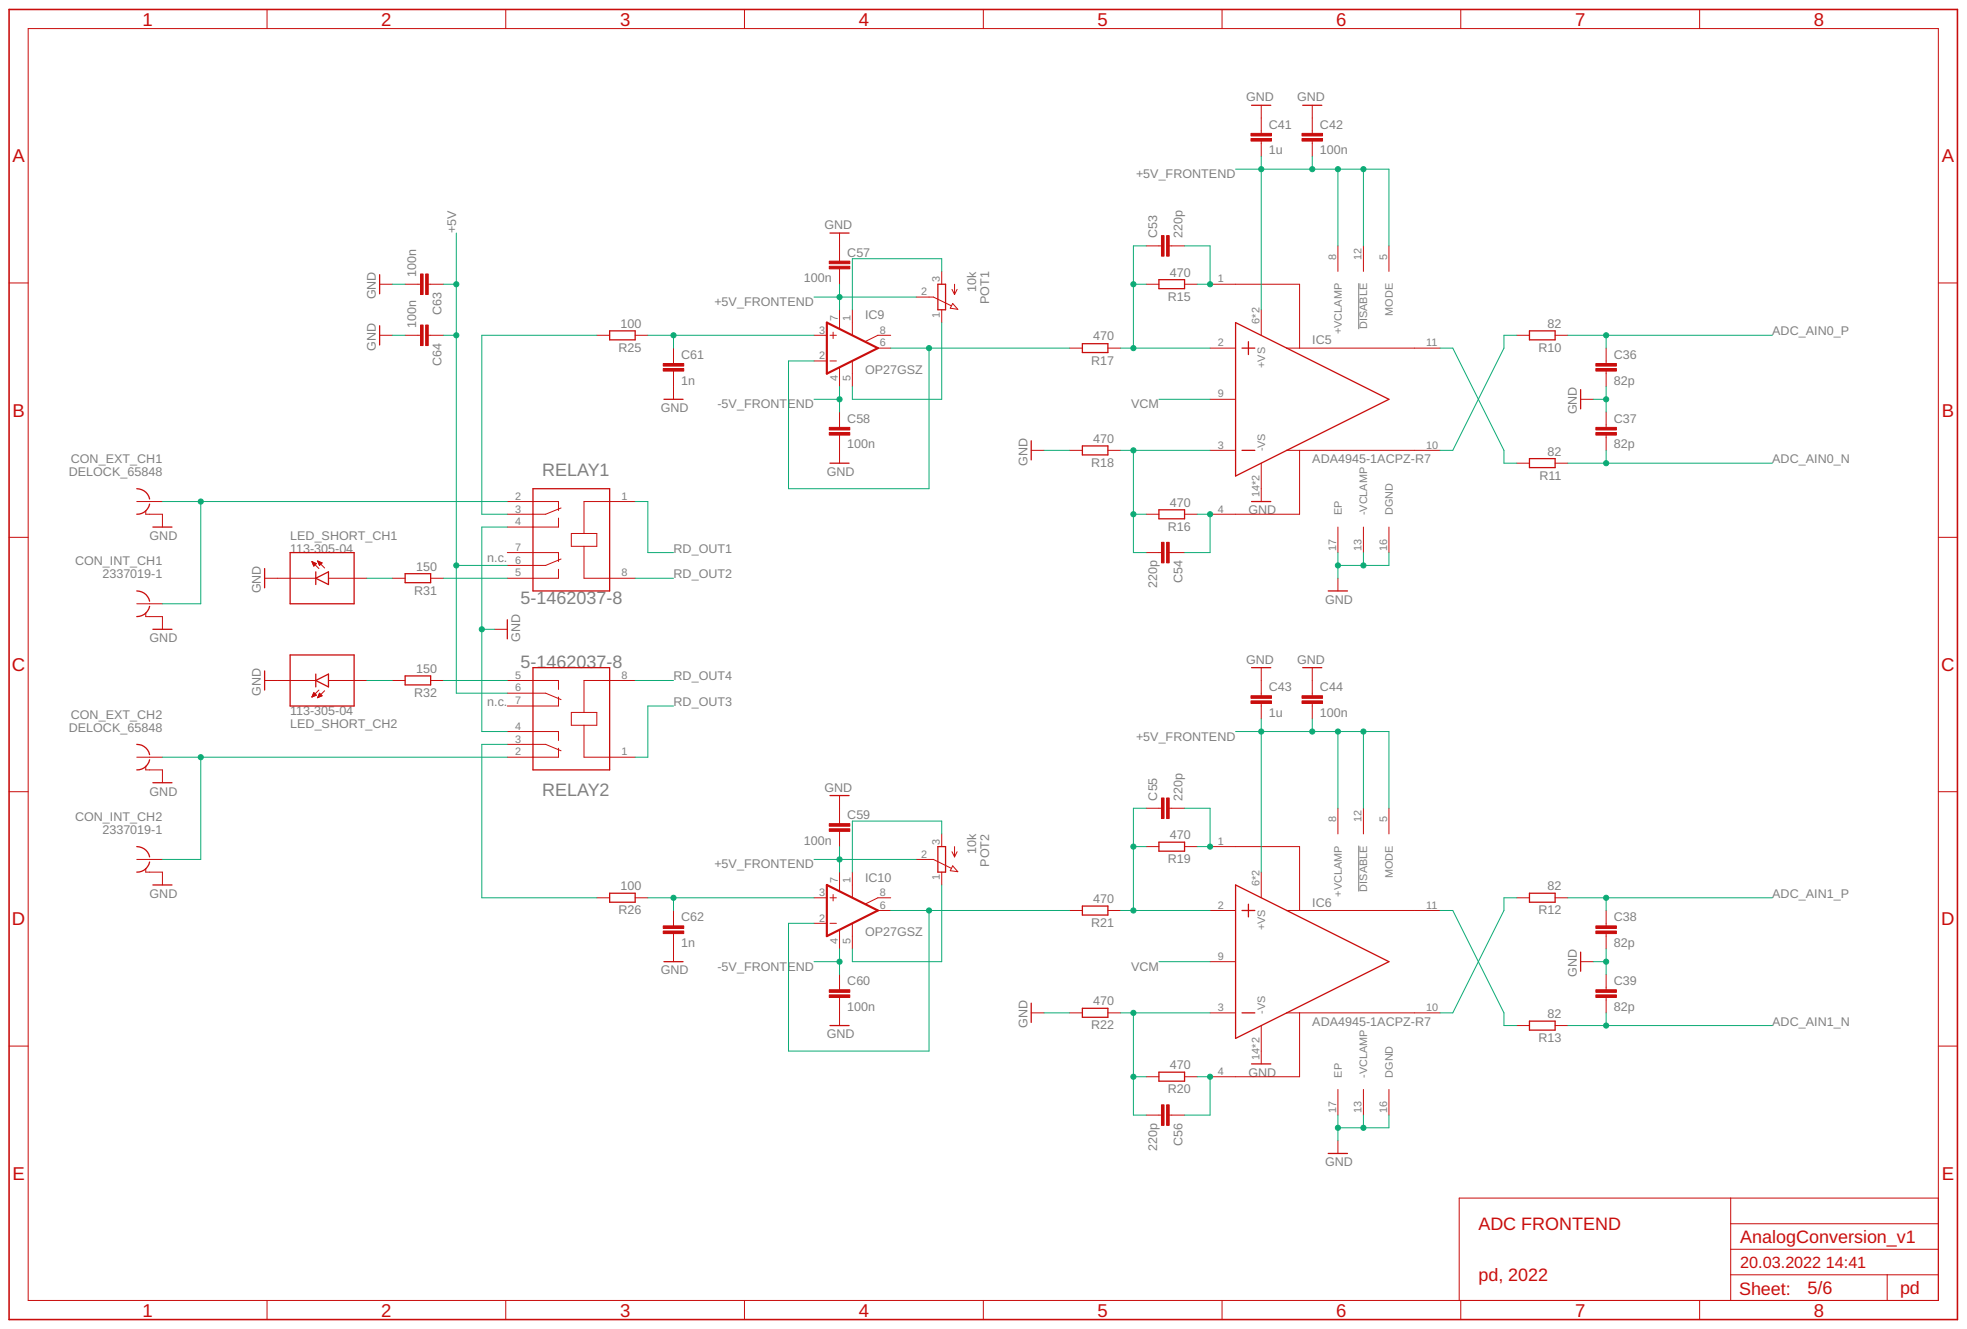
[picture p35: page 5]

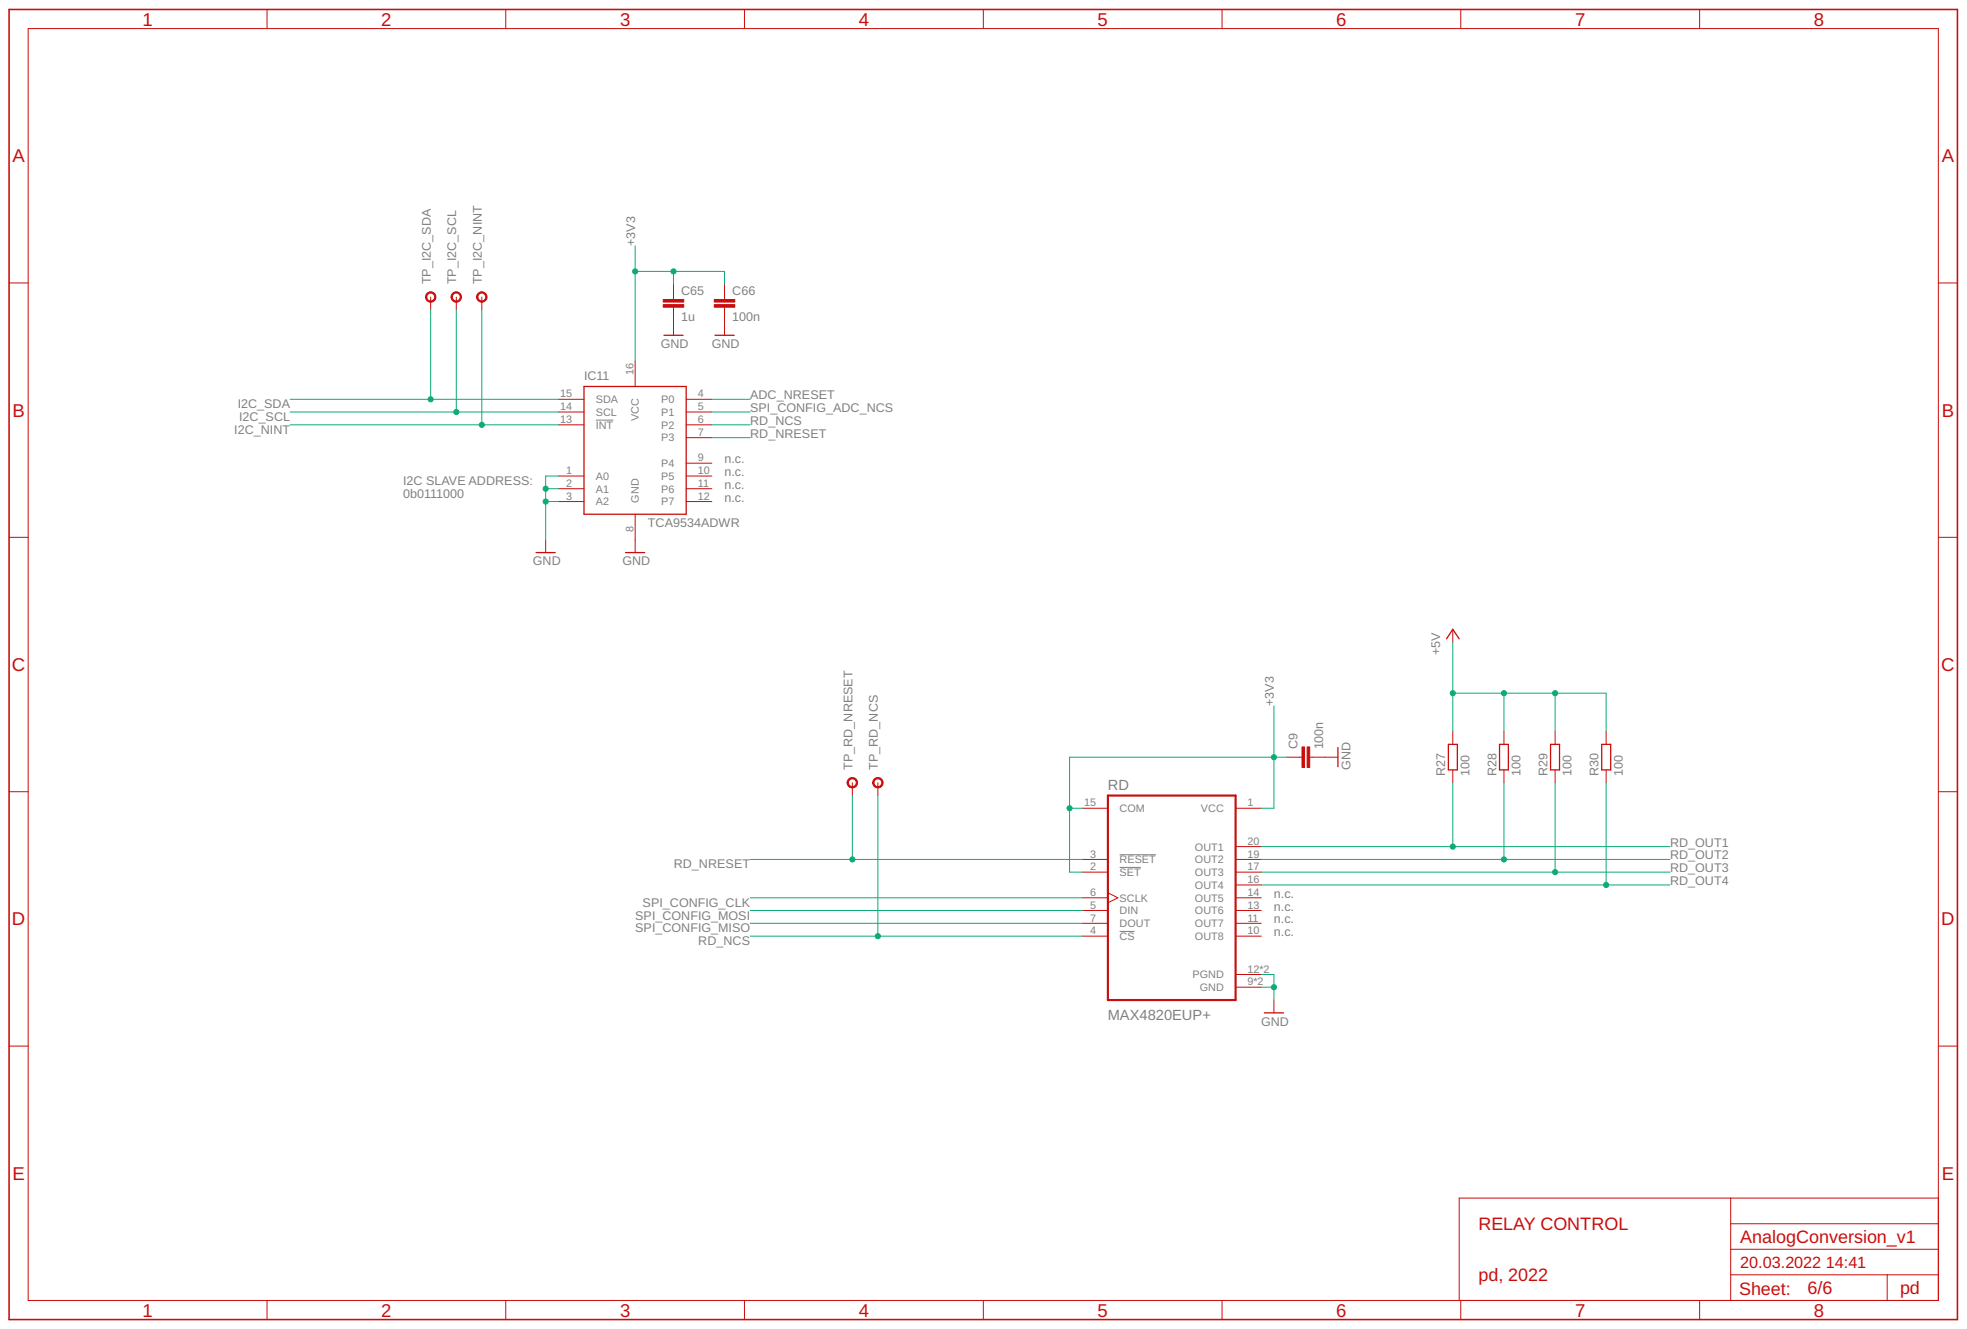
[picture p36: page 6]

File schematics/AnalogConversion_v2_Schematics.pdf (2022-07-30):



9 11 13 15 | 10

27 | 28
29 | 30
31 | 32

GND GND


Optional precision voltage reference

Green: 2 mA / 1.9 V


19 56 | DEC1/SDI 18 | 54

All channels output on the DOUT0 pin CMOS clock

3 ST | 21 DGND55 20

33 DNC/DGND



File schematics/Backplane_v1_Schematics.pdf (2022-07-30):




+5V +12V -12V TP_BITE_PS_+5V_CURRENT TP_BITE_PS_5V_TS1 TP_BITE_PS_5V_TS2 TP_BITE_PS_12V_TS1 TP_BITE_PS_12V_TS2 TP_+5V TP_+12V TP_-12V TP_SPI_DATA_NCS TP_SPI_DATA_CLK TP_SPI_DATA_MOSI TP_SPI_CONFIG_MISO TP_SPI_CONFIG_MOSI TP_SPI_CONFIG_CLK TP_I2C_NINT TP_I2C_SDA TP_I2C_SCL TP_USART_RX TP_USART_TX TP_+3V3_MCU TP_VBUS_USB_DATA TP_USB_DATA_DP TP_USB_DATA_DM BITE_PS_+5V_CURRENT BITE_PS_5V_TS1 BITE_PS_12V_TS1 BITE_PS_5V_TS2 BITE_PS_12V_TS2 SPI_DATA_NCS SPI_DATA_CLK SPI_DATA_MOSI SPI_CONFIG_MISO SPI_CONFIG_MOSI SPI_CONFIG_CLK I2C_NINT I2C_SDA I2C_SCL USART_RX USART_TX +3V3_MCU VBUS_USB_DATA USB_DATA_DP USB_DATA_DM TESTPINS pd, 2022 github.com/yildi1337 Sheet: pd ABCDE 1 2 3 4 5 6 7 8 ABCDE 1 2 3 4 5 6 7 8 Backplane_v1 20.03.2022 14:54 3/3

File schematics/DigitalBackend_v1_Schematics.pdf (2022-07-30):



9 11 13 15 | 10

GND GND



ESR < 1 Ohm Power supply supervisor enabled Boot from user flash Boot from system flash VBAT VDDA VDD33USB VREF+ STM32H753ZIT6 GND 1u GND 1u 100n 100n 100n 100n 100n 100n 100n 100n 100n 100n 100n 100n GND 1u 100n GND 4.7u 2.2u 2.2u GND 10k 10k GND 5.6p 5.6p XRCGB25M000F2P00R0 GND GND GND GND ABS05-32.768KHZ-T 15p 15p GND GND GND 1.5k 1.5k 1.5k PE2 1 PE3 2 PE4 3 PE5 4 PE6 5 VBAT 6 PC13 7 PC14-OSC32_IN 8 PC15-OSC32_OUT 9 VSS 16*9 VDD 17*11 PF0 10 PF1 11 PF2 12 PF3 13 PF4 14 PF5 15 PF6 18 PF7 19 PF8 20 PF9 21 PF10 22 PH0-OSC_IN 23 PH1-OSC_OUT 24 NRST 25 PC1 27 PC0 26 PC2_C 28 PC3_C 29 VSSA 31 VREF+ 32 VDDA 33 PA0 34 PA1 35 PA2 36 PC4 44 PC5 45 VCAP 71*2 VDD33USB 95 PE0 141 PE1 142 PC6 96 PC7 97 PC8 98 PC9 99 PC10 111 PC11 112 PC12 113 BOOT0 138 PDR_ON 143 PA3 37 PA4 40 PA5 41 PA6 42 PA7 43 PB0 46 PB1 47 PB2 48 PF11 49 PF12 50 PF13 53 PF14 54 PF15 55 PG0 56 PG1 57 PE7 58 PE8 59 PE9 60 PE10 63 PE11 64 PE12 65 PE13 66 PE14 67 PE15 68 PB10 69 PB11 70 PB12 73 PB13 74 PB14 75 PB15 76 PD8 77 PD9 78 PD10 79 PD11 80 PD12 81 PD13 82 PD14 85 PD15 86 PG2 87 PG3 88 PG4 89 PG5 90 PG6 91 PG7 92 PG8 93 PA8 100 PA9 101 PA10 102 PA11 103 PA12 104 PA13 105 PA14 109 PA15 110 PD1 115 PD2 116 PD3 117 PD4 118 PD5 119 PD0 114 PD6 122 PD7 123 PG9 124 PG10 125 PG11 126 PG12 127 PG13 128 PG14 129 PG15 132 PB3 133 PB4 134 PB5 135 PB6 136 PB7 137 PB8 139 PB9 140 MCU C11 C12 C13 C16 C17 C18 C19 C20 C21 C22 C23 C24 C25 C26 C27 C28 C29 C30 C31 R3 3 1 2 SJ1 R4 C43 C44 XTAL1 1 2 XTAL2 C45 C46 R8 R9 R10 +3V3_VDD +3V3_VDD +3V3_VDD +3V3_VDD +3V3_VDD +3V3_VDD +3V3_VDD +3V3_VDD +3V3_VDD +3V3_VDDA +3V3_VDDA NJTRST JTDI JTMS/SWDIO JTCK/SWCLK JTDO/TRACESWO ULPI_STP ULPI_NXT ULPI_DIR ULPI_CLK ULPI_DATA0 ULPI_DATA1 ULPI_DATA2 ULPI_DATA3 ULPI_DATA4 ULPI_DATA5 ULPI_DATA6 ULPI_DATA7 NRST SPI2_MOSI SPI2_SCK SPI2_NSS SPI3_MISO SPI3_MOSI SPI3_SCK USART1_TX USART1_RX DEBUG1 DEBUG2 DEBUG3 DEBUG4 I2C4_SCL I2C4_SCL I2C4_SDA I2C4_SDA VCAP VCAP I2C4_NINT I2C4_NINT LED1 LED2 LED3 LED4 MCU pd, 2022 pd github.com/yildi1337 Sheet: ABCDE 1 2 3 4 5 6 7 8 ABCDE 1 2 3 4 5 6 7 8 DigitalBackend_v1 09.04.2022 12:57 4/6



Yellow: 2 mA / 1.85 V Yellow: 2 mA / 1.85 V Yellow: 2 mA / 1.85 V Yellow: 2 mA / 1.85 V GND 10k 10k 10k TST-110-01-T-DJ GND 750 GND 750 GND 750 GND 750 GND 100n GND GND GND TP33W008000 74LVC126AD,112 74LVC126AD,112 74LVC126AD,112 74LVC126AD,112 100n GND 68686868 GND 113-314-04 GND 113-314-04 GND 113-314-04 GND 113-314-04 R5 R6 R7 1 1 2 2 3 3 4 4 5 5 6 6 7 7 8 8 9 9 10 10 11 11 12 12 13 13 14 14 15 15 16 16 17 17 18 18 19 19 20 20 CON_JTAG TP_DEBUG1 TP_DEBUG2 TP_DEBUG3 TP_DEBUG4 LED_DEBUG1 R64 LED_DEBUG2 R65 LED_DEBUG3 R66 LED_DEBUG4 R67 C32 GND1 GND2SW_RST_MCU 1 2 3 IC5A 4 5 6 IC5B 10 9 8 IC5C 13 12 11 IC5D GND VCC 7 14 IC5P C93 R60 R61 R62 R63 LED1 LED2 LED3 LED4 +3V3_VDD +3V3_VDD +3V3_VDD NJTRST JTDI JTMS/SWDIO JTCK/SWCLK JTDO/TRACESWO NRST NRST DEBUG1 DEBUG2 DEBUG3 DEBUG4 LED1 LED2 LED3 LED4 DEBUG pd, 2022 Sheet: pd ABCDE 1 2 3 4 5 6 7 8 ABCDE 1 2 3 4 5 6 7 8 DigitalBackend_v1 09.04.2022 12:57 6/6

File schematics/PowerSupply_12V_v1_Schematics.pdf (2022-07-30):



9 11 13 15 | 10

17 | 18
19 | 20
21 | 22
23 | 24
25 27 29 | 26 28 30

GND GND


RSPRO-SPDT-SLIDE-SWITCH-7347334 360/2W

RSPRO-SPDT-SLIDE-SWITCH-7347334

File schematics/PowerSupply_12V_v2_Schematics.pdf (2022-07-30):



9 11 13 15 | 10

17 | 18
19 | 20
21 | 22
23 | 24
25 27 29 | 26 28 30


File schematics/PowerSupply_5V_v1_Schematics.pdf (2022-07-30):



9 11 13 15 | 10

17 | 18
19 | 20
21 | 22
23 | 24
25 27 29 | 26 28 30

GND GND


RSPRO-SPDT-SLIDE-SWITCH-7347334 82/2W

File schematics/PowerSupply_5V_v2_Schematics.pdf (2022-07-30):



9 11 13 15 | 10

17 | 18
19 | 20
21 | 22
23 | 24
25 27 29 | 26 28 30


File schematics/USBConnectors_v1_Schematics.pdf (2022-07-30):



15 | USB-B_DEBUG_DP 3


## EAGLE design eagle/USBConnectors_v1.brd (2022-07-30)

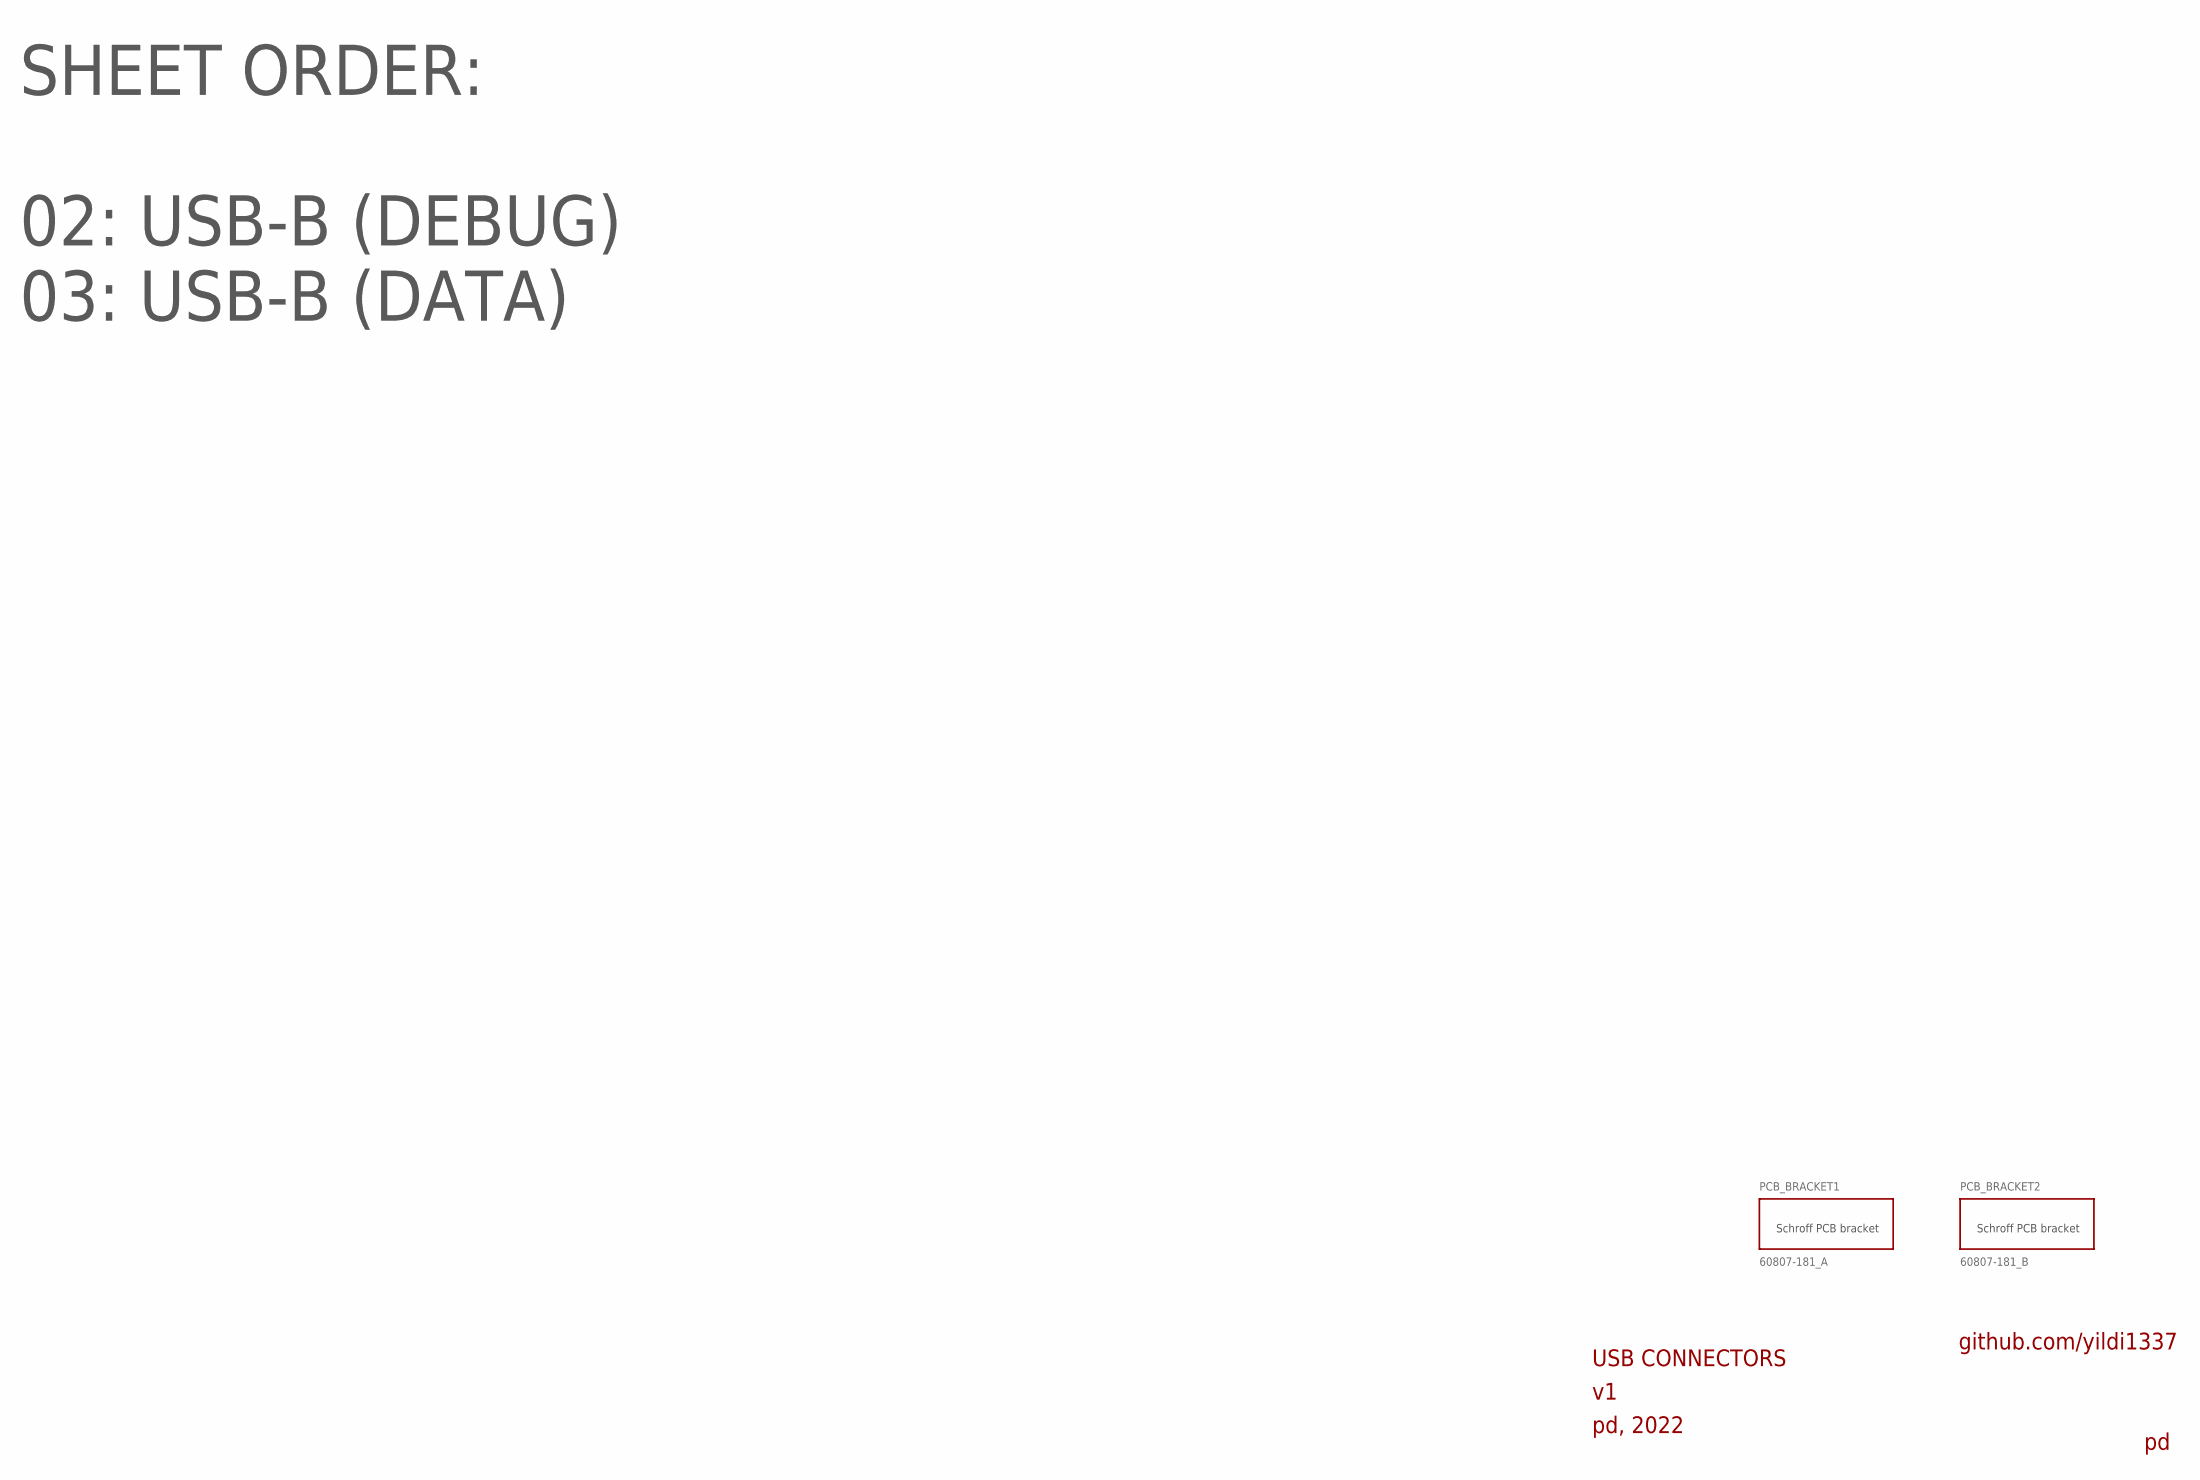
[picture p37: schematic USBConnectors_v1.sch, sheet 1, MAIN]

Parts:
PCB_BRACKET1: 60807-181_A
PCB_BRACKET2: 60807-181_B

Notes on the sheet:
USB CONNECTORS
pd, 2022
github.com/yildi1337
SHEET ORDER: 02: USB-B (DEBUG) 03: USB-B (DATA)

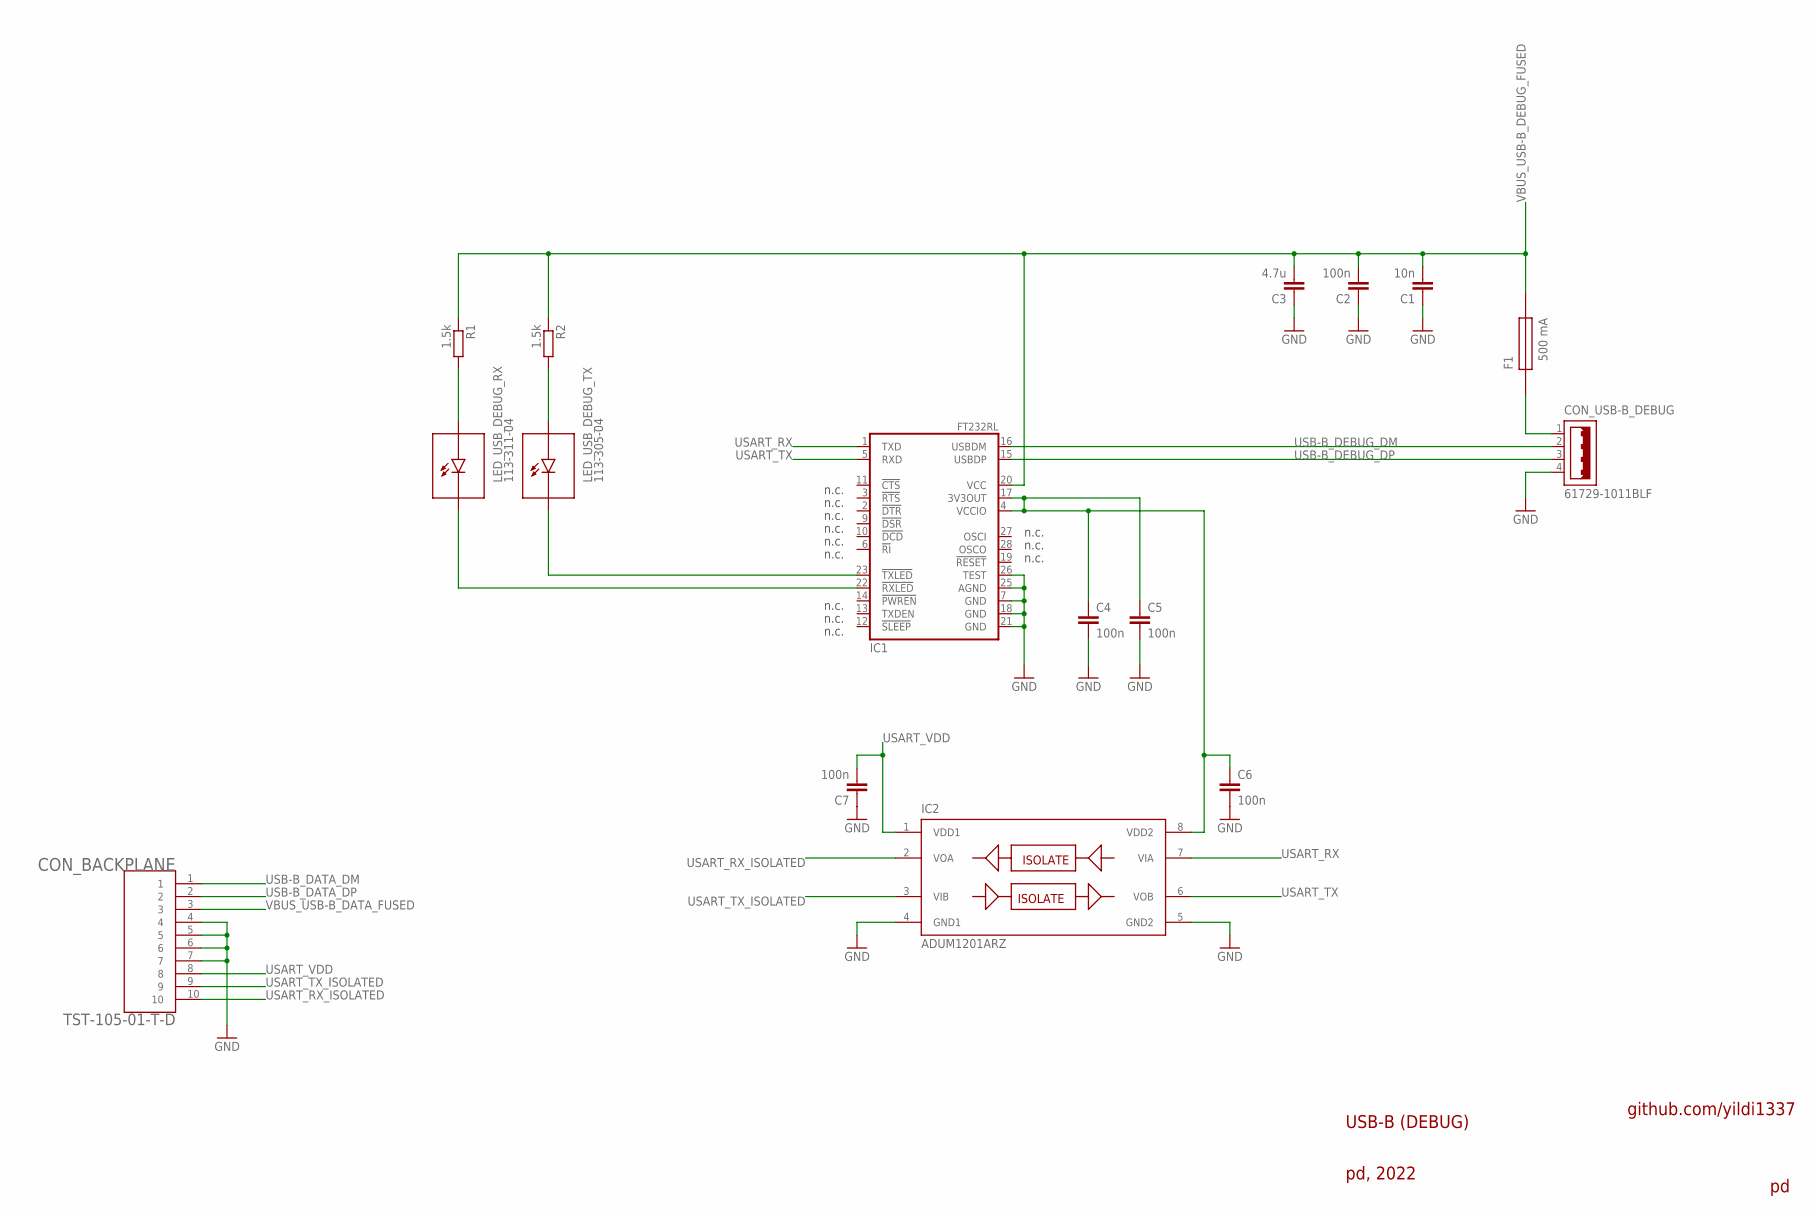
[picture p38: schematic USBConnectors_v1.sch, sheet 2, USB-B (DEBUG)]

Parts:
C1: 10n; C0603
C2, C4, C5, C6, C7: 100n; C0603
C3: 4.7u; C0603
CON_BACKPLANE: TST-105-01-T-D
CON_USB-B_DEBUG: 61729-1011BLF
F1: 500 mA; LITTELFUSE_466_SERIES
IC1: FT232RL
IC2: ADUM1201ARZ; SO8
LED_USB_DEBUG_RX: 113-311-04
LED_USB_DEBUG_TX: 113-305-04
R1, R2: 1.5k; R0603

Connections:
GND: C1.2, C2.1, C3.1, C4.2, C5.2, C6.2, C7.1, CON_BACKPLANE.4, CON_BACKPLANE.5, CON_BACKPLANE.6, CON_BACKPLANE.7, CON_USB-B_DEBUG.4, IC1.7 (GND), IC1.18 (GND), IC1.21 (GND), IC1.25 (AGND), IC1.26 (TEST), IC2.4 (GND1), IC2.5 (GND2); also elsewhere on the board
unnamed: CON_USB-B_DEBUG.1, F1.1
unnamed: LED_USB_DEBUG_RX.+ (A), R1.2
unnamed: LED_USB_DEBUG_TX.+ (A), R2.2
unnamed: C4.1, C5.1, C6.1, IC1.4 (VCCIO), IC1.17 (3V3OUT), IC2.8 (VDD2)
unnamed: IC1.22 (!RXLED), LED_USB_DEBUG_RX.- (C)
unnamed: IC1.23 (!TXLED), LED_USB_DEBUG_TX.- (C)
USART_RX: IC1.1 (TXD), IC2.7 (VIA)
USART_RX_ISOLATED: CON_BACKPLANE.10, IC2.2 (VOA)
USART_TX: IC1.5 (RXD), IC2.6 (VOB)
USART_TX_ISOLATED: CON_BACKPLANE.9, IC2.3 (VIB)
USART_VDD: C7.2, CON_BACKPLANE.8, IC2.1 (VDD1)
USB-B_DATA_DM: CON_BACKPLANE.1; also elsewhere on the board
USB-B_DATA_DP: CON_BACKPLANE.2; also elsewhere on the board
USB-B_DEBUG_DM: CON_USB-B_DEBUG.2, IC1.16 (USBDM)
USB-B_DEBUG_DP: CON_USB-B_DEBUG.3, IC1.15 (USBDP)
VBUS_USB-B_DATA_FUSED: CON_BACKPLANE.3; also elsewhere on the board
VBUS_USB-B_DEBUG_FUSED: C1.1, C2.2, C3.2, F1.2, IC1.20 (VCC), R1.1, R2.1

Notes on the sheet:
n.c.
USB-B (DEBUG)
pd, 2022
github.com/yildi1337

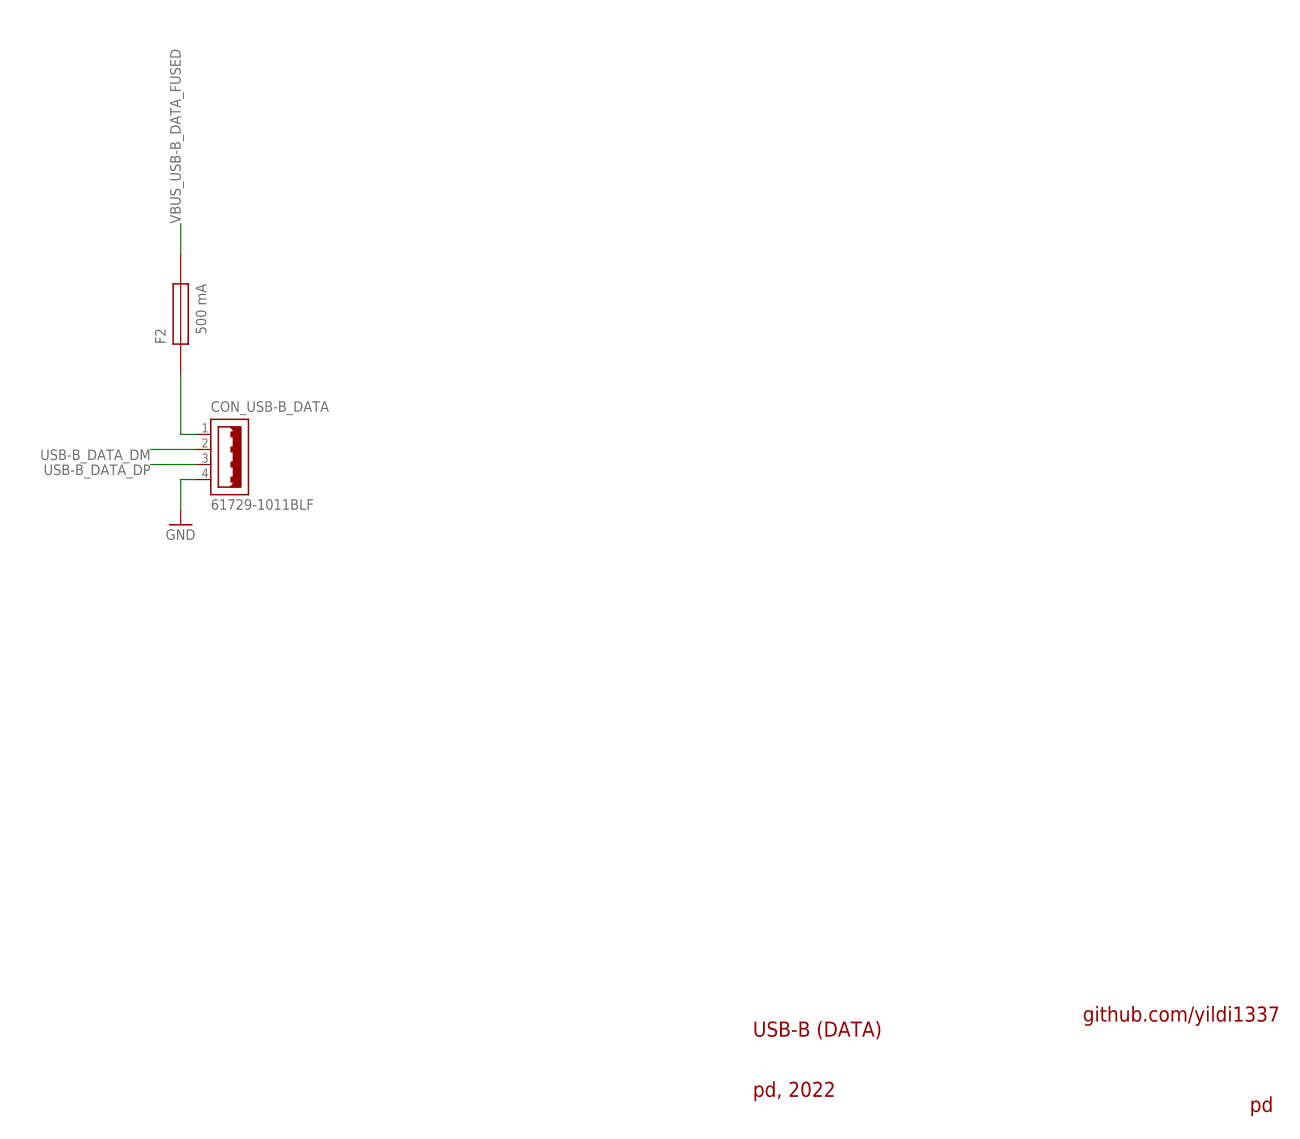
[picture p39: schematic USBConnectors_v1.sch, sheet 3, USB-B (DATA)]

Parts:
CON_USB-B_DATA: 61729-1011BLF
F2: 500 mA; LITTELFUSE_466_SERIES

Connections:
GND: CON_USB-B_DATA.4; also elsewhere on the board
USB-B_DATA_DM: CON_USB-B_DATA.2; also elsewhere on the board
USB-B_DATA_DP: CON_USB-B_DATA.3; also elsewhere on the board
VBUS_USB-B_DATA_FUSED: F2.2; also elsewhere on the board
VBUS_USB-B_NF: CON_USB-B_DATA.1, F2.1

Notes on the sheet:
USB-B (DATA)
pd, 2022
github.com/yildi1337

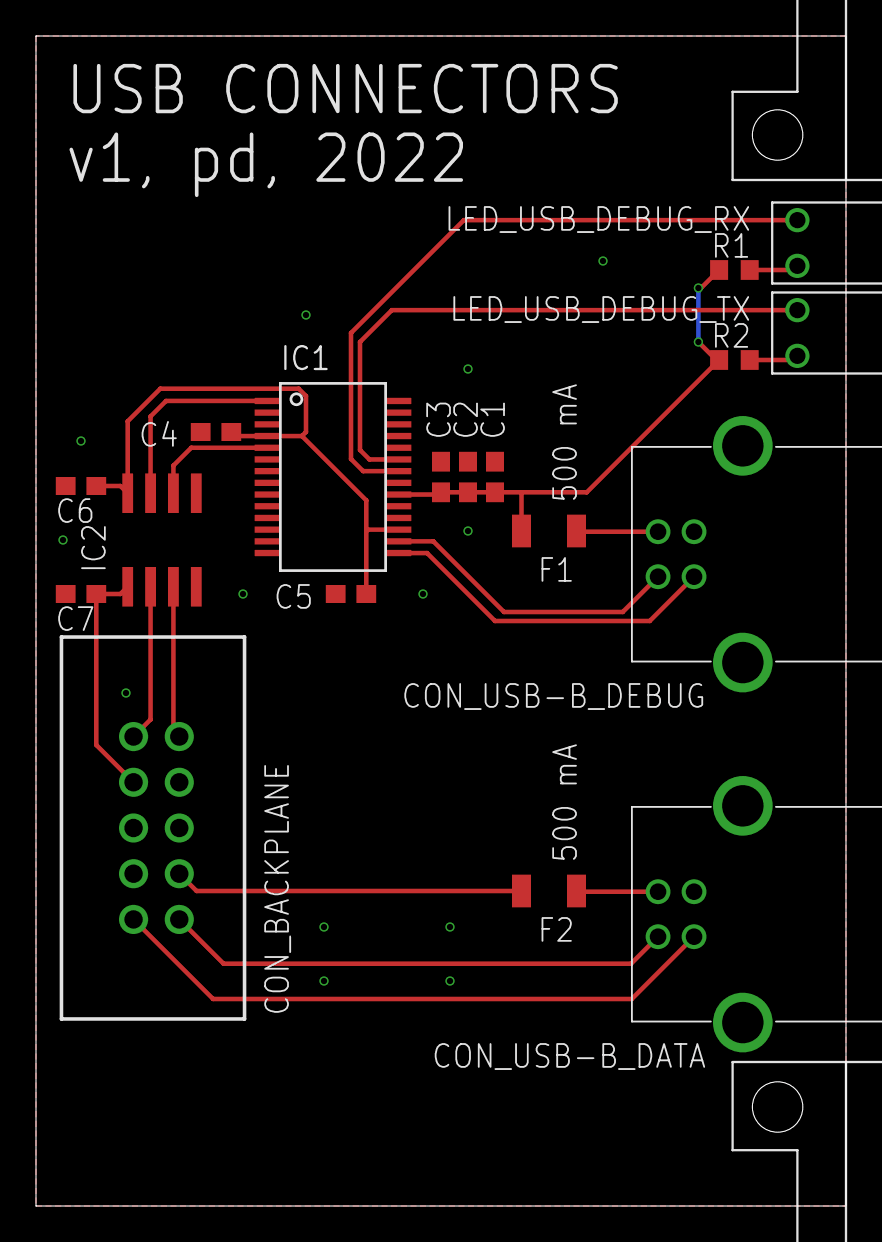
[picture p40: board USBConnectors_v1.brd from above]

Board: 2 copper layers, 45.0 x 65.0 mm, 20 parts (0 on the bottom side), 19 nets.

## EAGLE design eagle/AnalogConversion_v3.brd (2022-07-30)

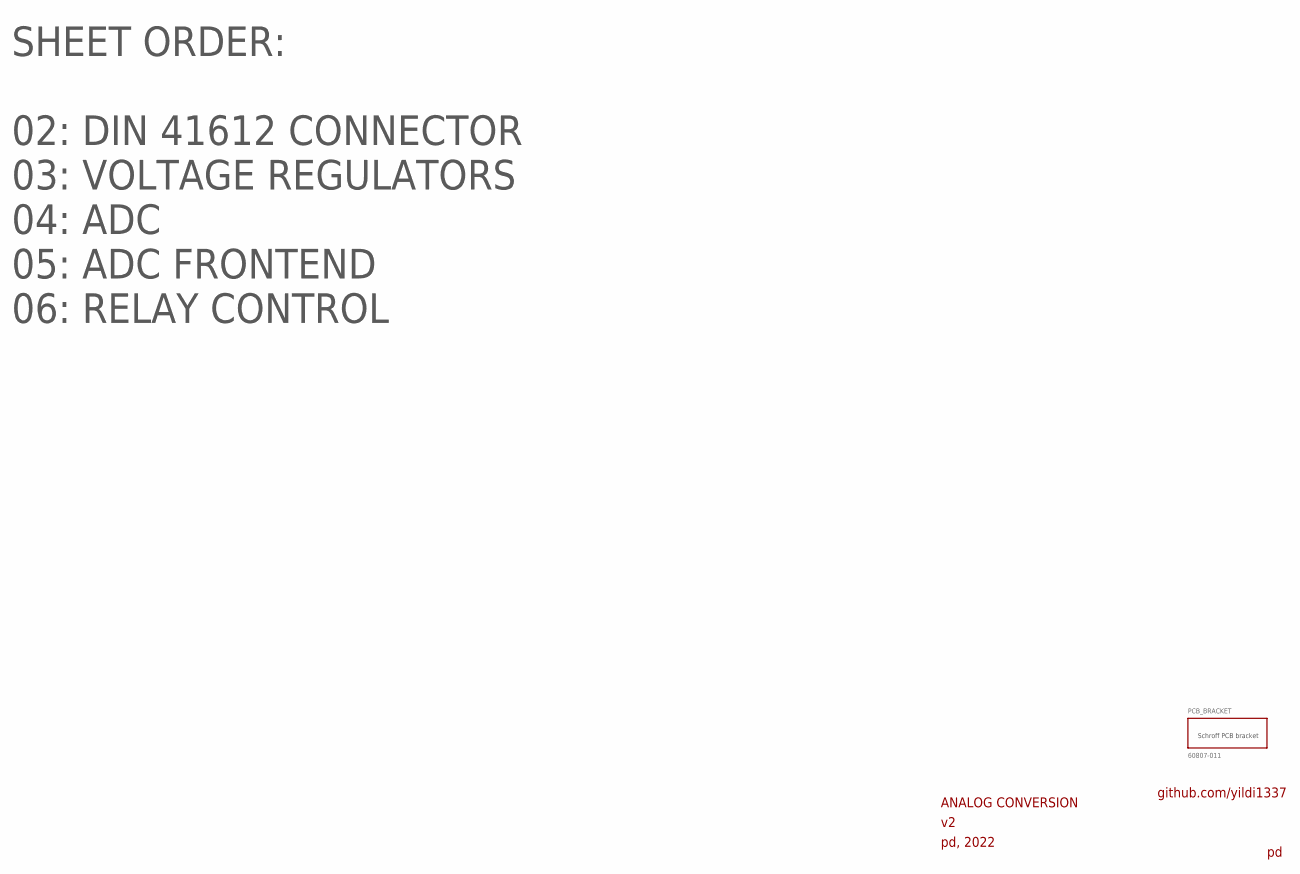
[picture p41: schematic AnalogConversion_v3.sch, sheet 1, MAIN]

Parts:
PCB_BRACKET: 60807-011

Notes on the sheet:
ANALOG CONVERSION
pd, 2022
github.com/yildi1337
SHEET ORDER: 02: DIN 41612 CONNECTOR 03: VOLTAGE REGULATORS 04: ADC 05: ADC FRONTEND 06: RELAY CONTROL

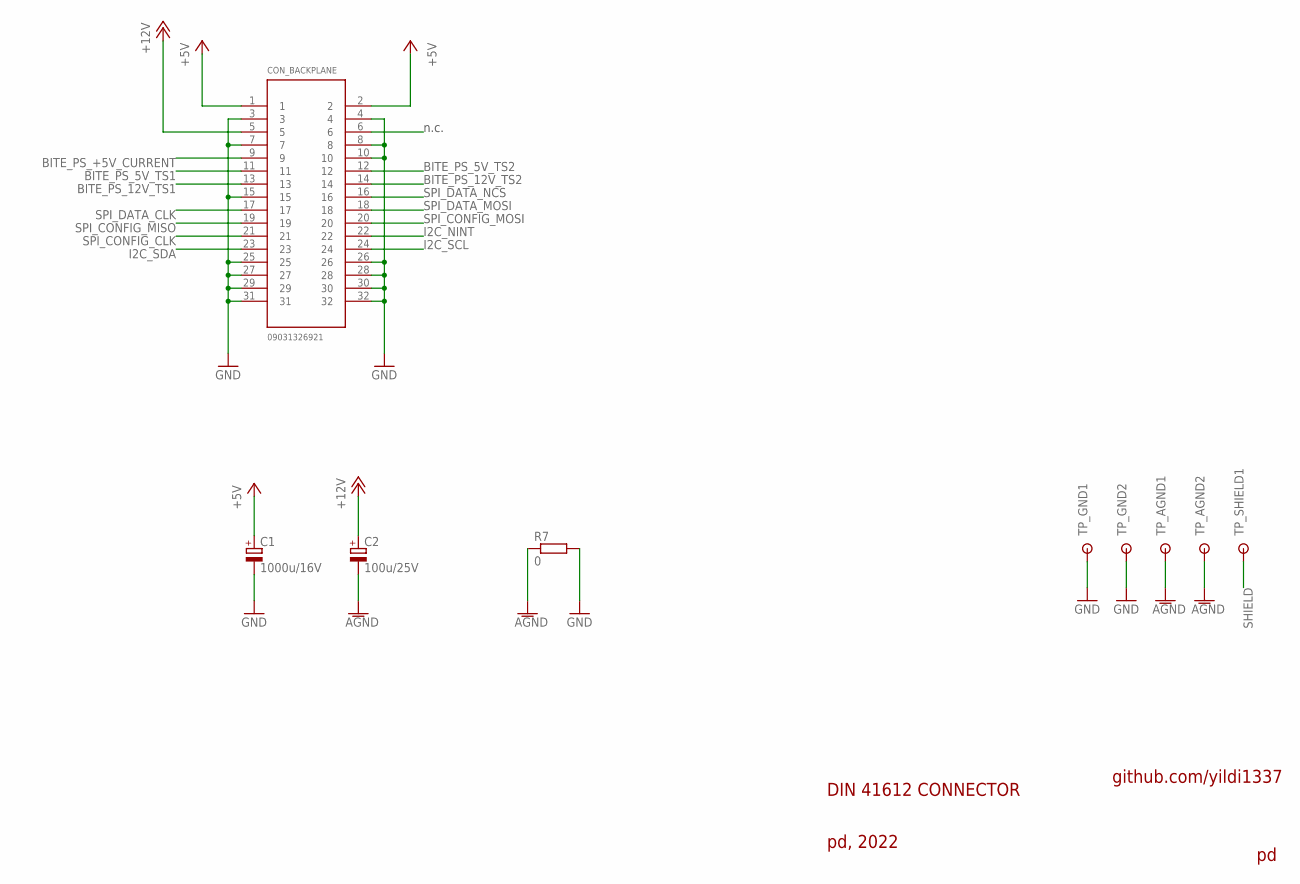
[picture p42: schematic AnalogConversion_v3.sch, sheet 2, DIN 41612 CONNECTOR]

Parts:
C1: 1000u/16V; 153CLV-1010
C2: 100u/25V; 153CLV-0810
CON_BACKPLANE: 09031326921
R7: 0; R0603
TP_AGND1, TP_AGND2: RSPRO-1MM-TERMINAL-POST-2622034
TP_GND1, TP_GND2: RSPRO-1MM-TERMINAL-POST-2622034
TP_SHIELD1: RSPRO-1MM-TERMINAL-POST-2622034

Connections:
+5V: C1.+, CON_BACKPLANE.1, CON_BACKPLANE.2; also elsewhere on the board
+12V: C2.+, CON_BACKPLANE.5; also elsewhere on the board
AGND: C2.-, R7.1, TP_AGND1.P$1, TP_AGND2.P$1; also elsewhere on the board
BITE_PS_5V_TS1: CON_BACKPLANE.11
BITE_PS_5V_TS2: CON_BACKPLANE.12
BITE_PS_12V_TS1: CON_BACKPLANE.13
BITE_PS_12V_TS2: CON_BACKPLANE.14
BITE_PS_+5V_CURRENT: CON_BACKPLANE.9
GND: C1.-, CON_BACKPLANE.3, CON_BACKPLANE.4, CON_BACKPLANE.7, CON_BACKPLANE.8, CON_BACKPLANE.10, CON_BACKPLANE.15, CON_BACKPLANE.25, CON_BACKPLANE.26, CON_BACKPLANE.27, CON_BACKPLANE.28, CON_BACKPLANE.29, CON_BACKPLANE.30, CON_BACKPLANE.31, CON_BACKPLANE.32, R7.2, TP_GND1.P$1, TP_GND2.P$1; also elsewhere on the board
I2C_NINT: CON_BACKPLANE.22; also elsewhere on the board
I2C_SCL: CON_BACKPLANE.24; also elsewhere on the board
I2C_SDA: CON_BACKPLANE.23; also elsewhere on the board
SHIELD: TP_SHIELD1.P$1; also elsewhere on the board
SPI_CONFIG_CLK: CON_BACKPLANE.21; also elsewhere on the board
SPI_CONFIG_MISO: CON_BACKPLANE.19; also elsewhere on the board
SPI_CONFIG_MOSI: CON_BACKPLANE.20; also elsewhere on the board
SPI_DATA_CLK: CON_BACKPLANE.17; also elsewhere on the board
SPI_DATA_MOSI: CON_BACKPLANE.18; also elsewhere on the board
SPI_DATA_NCS: CON_BACKPLANE.16; also elsewhere on the board

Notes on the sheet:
DIN 41612 CONNECTOR
pd, 2022
github.com/yildi1337
n.c.

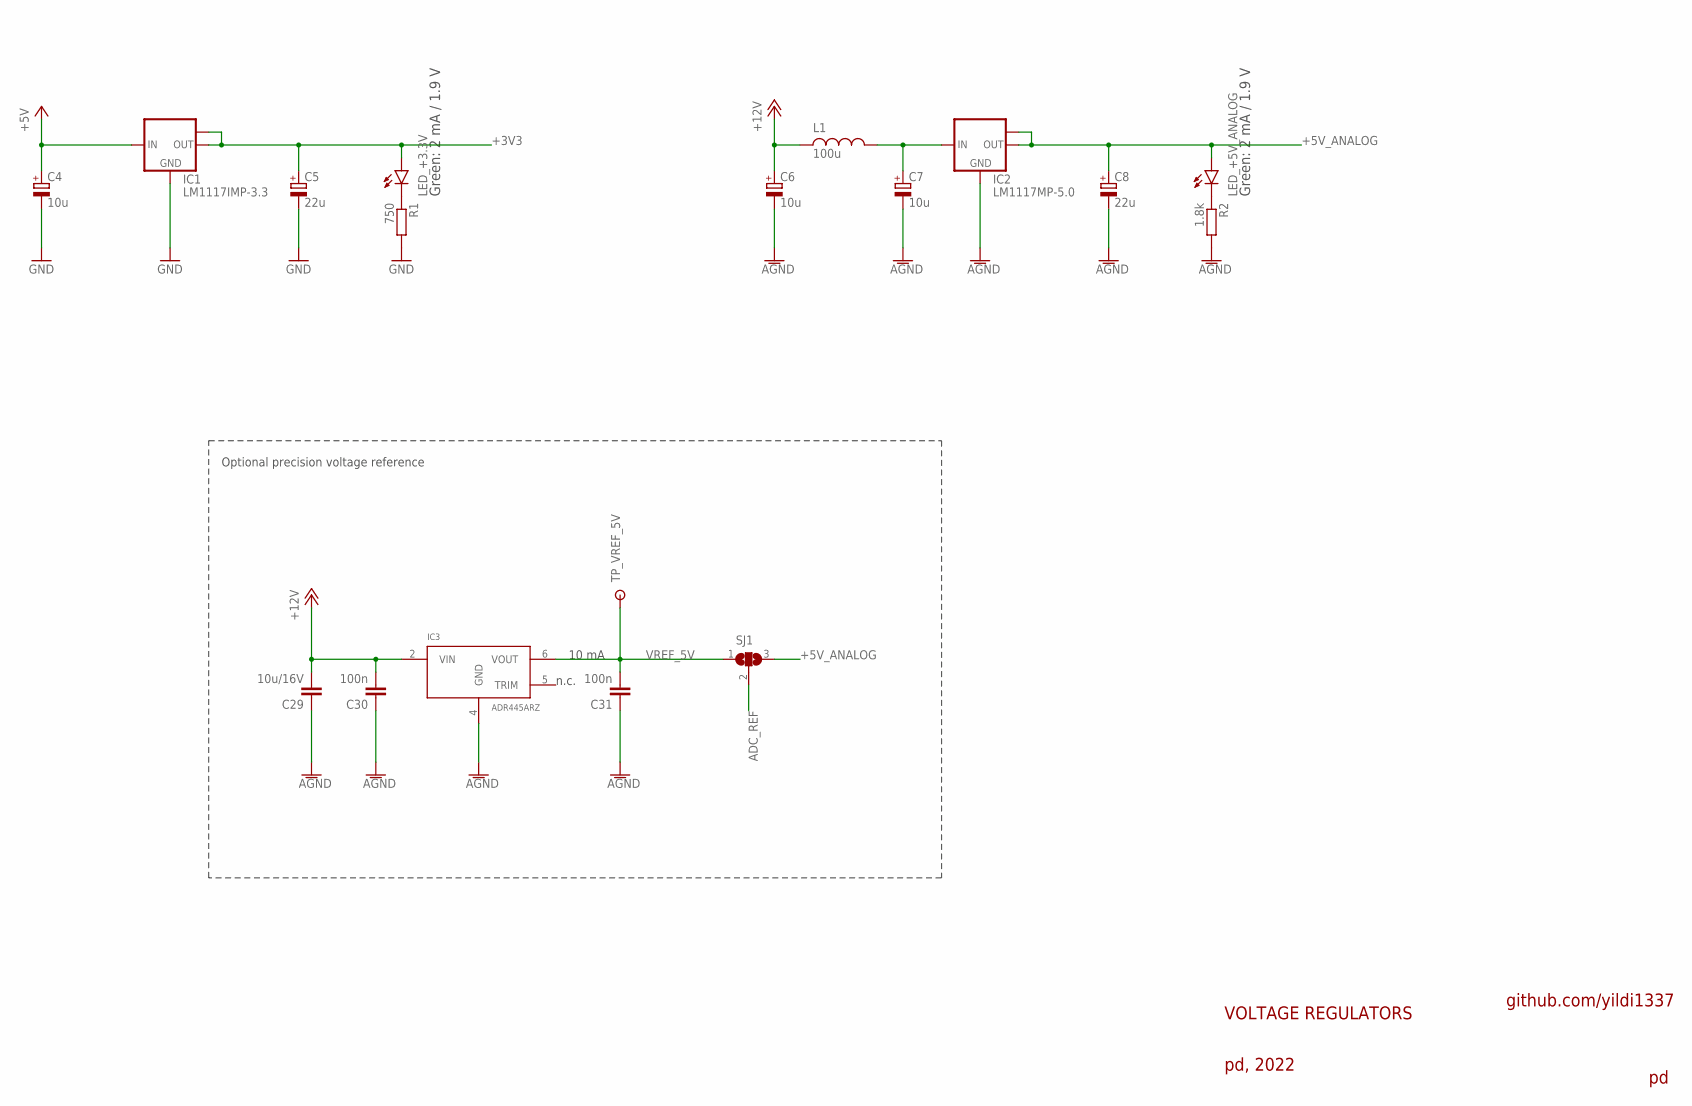
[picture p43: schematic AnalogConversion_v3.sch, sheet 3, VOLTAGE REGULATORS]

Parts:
C4, C6, C7: 10u; CT3216
C5, C8: 22u; CT6032
C29: 10u/16V; C0805
C30, C31: 100n; C0603
IC1: LM1117IMP-3.3; SOT223
IC2: LM1117MP-5.0; SOT223
IC3: ADR445ARZ
L1: 100u; VLS6045AF-101M
LED_+3.3V, LED_+5V_ANALOG: LEDCHIP-LED0603; CHIP-LED0603
R1: 750; R0603
R2: 1.8k; R0603
SJ1: SJ2W; SJ_2
TP_VREF_5V: RSPRO-1MM-TERMINAL-POST-2622034

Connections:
+3V3: C5.+, IC1.2 (OUT), IC1.TAB (OUT1), LED_+3.3V.A; also elsewhere on the board
+5V: C4.+, IC1.3 (IN); also elsewhere on the board
+5V_ANALOG: C8.+, IC2.2 (OUT), IC2.TAB (OUT1), LED_+5V_ANALOG.A, SJ1.3; also elsewhere on the board
+12V: C6.+, C29.2, C30.2, IC3.2 (VIN), L1.1; also elsewhere on the board
ADC_REF: SJ1.2; also elsewhere on the board
AGND: C6.-, C7.-, C8.-, C29.1, C30.1, C31.1, IC2.1 (GND), IC3.4 (GND), R2.2; also elsewhere on the board
GND: C4.-, C5.-, IC1.1 (GND), R1.2; also elsewhere on the board
unnamed: C7.+, IC2.3 (IN), L1.2
unnamed: LED_+3.3V.C, R1.1
unnamed: LED_+5V_ANALOG.C, R2.1
VREF_5V: C31.2, IC3.6 (VOUT), SJ1.1, TP_VREF_5V.P$1

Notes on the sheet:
VOLTAGE REGULATORS
pd, 2022
github.com/yildi1337
Green: 2 mA / 1.9 V
Optional precision voltage reference
10 mA
n.c.

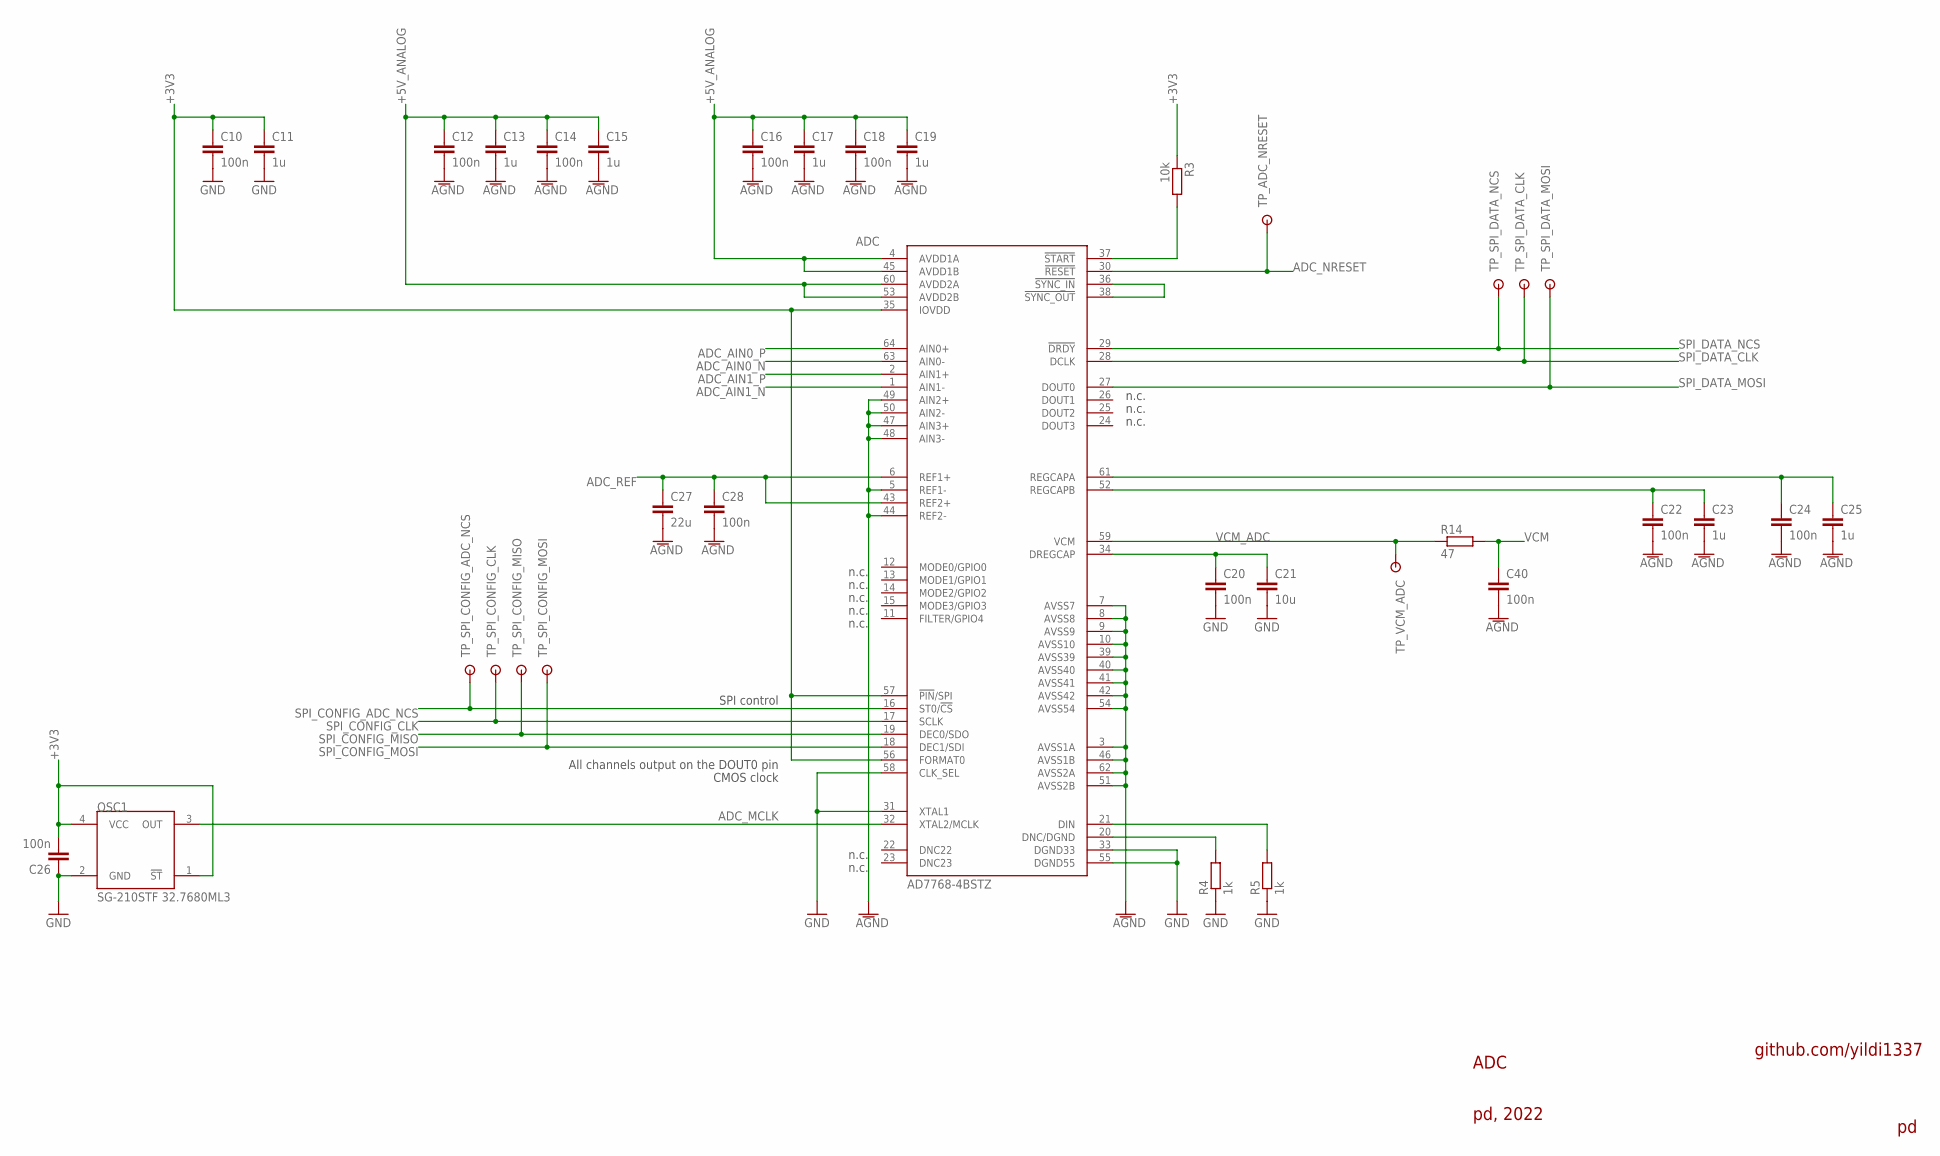
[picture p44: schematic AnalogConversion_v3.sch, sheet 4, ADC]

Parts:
ADC: AD7768-4BSTZ
C10, C12, C14, C16, C18, C20, C22, C24, C26, C28, C40: 100n; C0603
C11, C13, C15, C17, C19, C23, C25: 1u; C0603
C21: 10u; C0603
C27: 22u; C1206
OSC1: SG-210STF 32.7680ML3; SG-210STF-32.7680ML3
R3: 10k; R0603
R4, R5: 1k; R0603
R14: 47; R0603
TP_ADC_NRESET: RSPRO-1MM-TERMINAL-POST-2622034
TP_SPI_CONFIG_ADC_NCS: RSPRO-1MM-TERMINAL-POST-2622034
TP_SPI_CONFIG_CLK: RSPRO-1MM-TERMINAL-POST-2622034
TP_SPI_CONFIG_MISO: RSPRO-1MM-TERMINAL-POST-2622034
TP_SPI_CONFIG_MOSI: RSPRO-1MM-TERMINAL-POST-2622034
TP_SPI_DATA_CLK: RSPRO-1MM-TERMINAL-POST-2622034
TP_SPI_DATA_MOSI: RSPRO-1MM-TERMINAL-POST-2622034
TP_SPI_DATA_NCS: RSPRO-1MM-TERMINAL-POST-2622034
TP_VCM_ADC: RSPRO-1MM-TERMINAL-POST-2622034

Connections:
+3V3: ADC.35 (IOVDD), ADC.56 (FORMAT0), ADC.57 (!PIN!/SPI), C10.1, C11.1, C26.2, OSC1.1 (!ST), OSC1.4 (VCC), R3.1; also elsewhere on the board
+5V_ANALOG: ADC.4 (AVDD1A), ADC.45 (AVDD1B), ADC.53 (AVDD2B), ADC.60 (AVDD2A), C12.1, C13.1, C14.1, C15.1, C16.1, C17.1, C18.1, C19.1; also elsewhere on the board
ADC_AIN0_N: ADC.63 (AIN0-); also elsewhere on the board
ADC_AIN0_P: ADC.64 (AIN0+); also elsewhere on the board
ADC_AIN1_N: ADC.1 (AIN1-); also elsewhere on the board
ADC_AIN1_P: ADC.2 (AIN1+); also elsewhere on the board
ADC_MCLK: ADC.32 (XTAL2/MCLK), OSC1.3 (OUT)
ADC_NRESET: ADC.30 (!RESET!), TP_ADC_NRESET.P$1; also elsewhere on the board
ADC_REF: ADC.6 (REF1+), ADC.43 (REF2+), C27.1, C28.1; also elsewhere on the board
AGND: ADC.3 (AVSS1A), ADC.5 (REF1-), ADC.7 (AVSS7), ADC.8 (AVSS8), ADC.9 (AVSS9), ADC.10 (AVSS10), ADC.39 (AVSS39), ADC.40 (AVSS40), ADC.41 (AVSS41), ADC.42 (AVSS42), ADC.44 (REF2-), ADC.46 (AVSS1B), ADC.47 (AIN3+), ADC.48 (AIN3-), ADC.49 (AIN2+), ADC.50 (AIN2-), ADC.51 (AVSS2B), ADC.54 (AVSS54), ADC.62 (AVSS2A), C12.2, C13.2, C14.2, C15.2, C16.2, C17.2, C18.2, C19.2, C22.2, C23.2, C24.2, C25.2, C27.2, C28.2, C40.2; also elsewhere on the board
DIN: ADC.21 (DIN), R5.2
DNC/DGND: ADC.20 (DNC/DGND), R4.2
DREGCAP: ADC.34 (DREGCAP), C20.1, C21.1
GND: ADC.31 (XTAL1), ADC.33 (DGND33), ADC.55 (DGND55), ADC.58 (CLK_SEL), C10.2, C11.2, C20.2, C21.2, C26.1, OSC1.2 (GND), R4.1, R5.1; also elsewhere on the board
unnamed: ADC.36 (!SYNC_IN!), ADC.38 (!SYNC_OUT!)
unnamed: ADC.37 (!START!), R3.2
REGCAPA: ADC.61 (REGCAPA), C24.1, C25.1
REGCAPB: ADC.52 (REGCAPB), C22.1, C23.1
SPI_CONFIG_ADC_NCS: ADC.16 (ST0/!CS!), TP_SPI_CONFIG_ADC_NCS.P$1; also elsewhere on the board
SPI_CONFIG_CLK: ADC.17 (SCLK), TP_SPI_CONFIG_CLK.P$1; also elsewhere on the board
SPI_CONFIG_MISO: ADC.19 (DEC0/SDO), TP_SPI_CONFIG_MISO.P$1; also elsewhere on the board
SPI_CONFIG_MOSI: ADC.18 (DEC1/SDI), TP_SPI_CONFIG_MOSI.P$1; also elsewhere on the board
SPI_DATA_CLK: ADC.28 (DCLK), TP_SPI_DATA_CLK.P$1; also elsewhere on the board
SPI_DATA_MOSI: ADC.27 (DOUT0), TP_SPI_DATA_MOSI.P$1; also elsewhere on the board
SPI_DATA_NCS: ADC.29 (!DRDY!), TP_SPI_DATA_NCS.P$1; also elsewhere on the board
VCM: C40.1, R14.2; also elsewhere on the board
VCM_ADC: ADC.59 (VCM), R14.1, TP_VCM_ADC.P$1

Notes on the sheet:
ADC
pd, 2022
All channels output on the DOUT0 pin
CMOS clock
n.c.
SPI control
github.com/yildi1337

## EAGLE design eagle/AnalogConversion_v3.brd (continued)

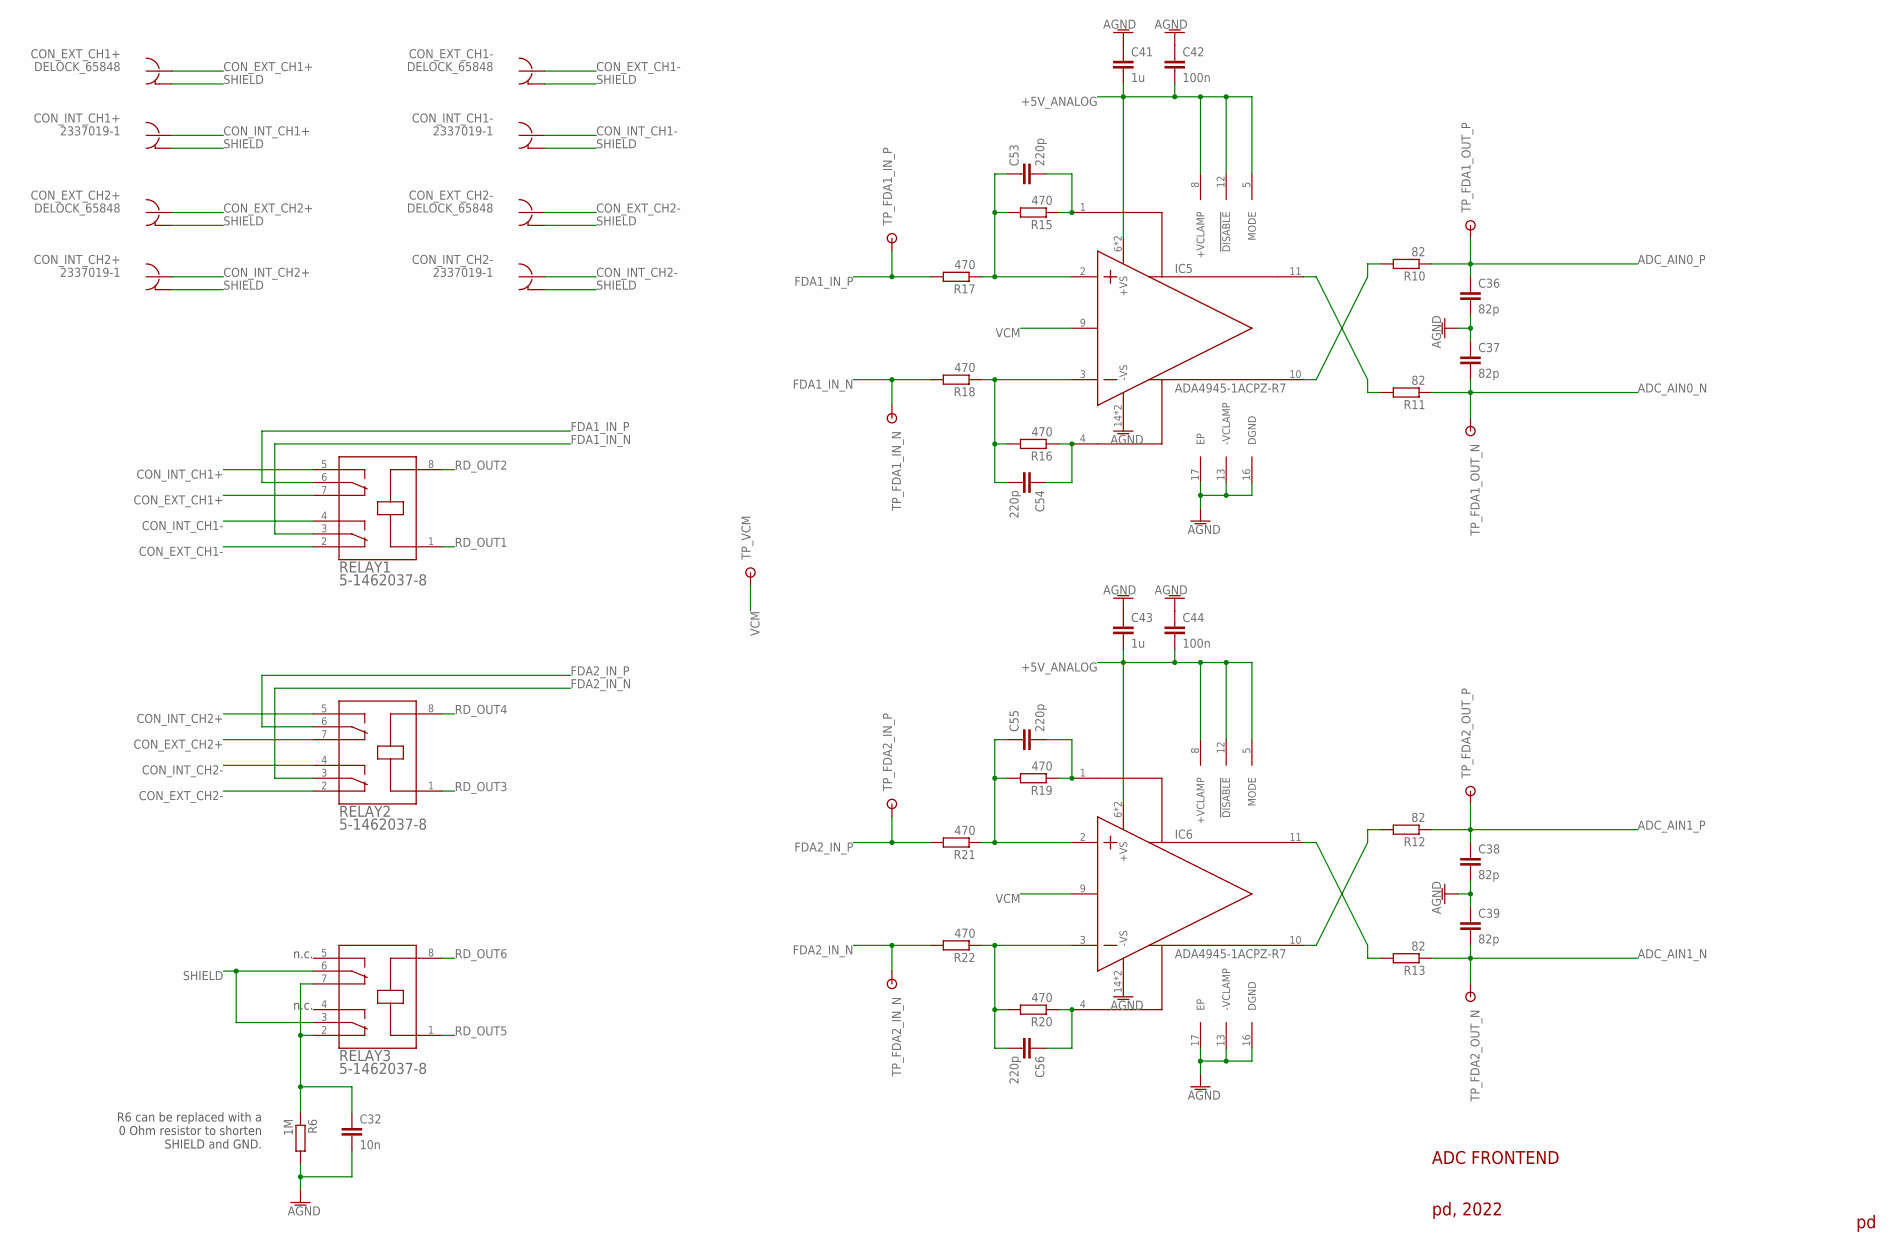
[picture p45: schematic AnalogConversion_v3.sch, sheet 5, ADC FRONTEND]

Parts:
C32: 10n; C0603
C36, C37, C38, C39: 82p; C0603
C41, C43: 1u; C0603
C42, C44: 100n; C0603
C53, C54, C55, C56: 220p; C0603
CON_EXT_CH1+, CON_EXT_CH1-, CON_EXT_CH2+, CON_EXT_CH2-: DELOCK_65848
CON_INT_CH1+, CON_INT_CH1-, CON_INT_CH2+, CON_INT_CH2-: 2337019-1
IC5, IC6: ADA4945-1ACPZ-R7
R6: 1M; R0603
R10, R11, R12, R13: 82; R0603
R15, R16, R17, R18, R19, R20, R21, R22: 470; R0603
RELAY1, RELAY2, RELAY3: 5-1462037-8
TP_FDA1_IN_N, TP_FDA1_IN_P, TP_FDA1_OUT_N, TP_FDA1_OUT_P, TP_FDA2_IN_N, TP_FDA2_IN_P, TP_FDA2_OUT_N, TP_FDA2_OUT_P: RSPRO-1MM-TERMINAL-POST-2622034
TP_VCM: RSPRO-1MM-TERMINAL-POST-2622034

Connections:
+5V_ANALOG: C41.2, C42.2, C43.2, C44.2, IC5.5 (MODE), IC5.6 (+VS), IC5.7 (+VS), IC5.8 (+VCLAMP), IC5.12 (!DISABLE), IC6.5 (MODE), IC6.6 (+VS), IC6.7 (+VS), IC6.8 (+VCLAMP), IC6.12 (!DISABLE); also elsewhere on the board
ADC_AIN0_N: C37.2, R11.1, TP_FDA1_OUT_N.P$1; also elsewhere on the board
ADC_AIN0_P: C36.1, R10.1, TP_FDA1_OUT_P.P$1; also elsewhere on the board
ADC_AIN1_N: C39.2, R13.1, TP_FDA2_OUT_N.P$1; also elsewhere on the board
ADC_AIN1_P: C38.1, R12.1, TP_FDA2_OUT_P.P$1; also elsewhere on the board
AGND: C32.2, C36.2, C37.1, C38.2, C39.1, C41.1, C42.1, C43.1, C44.1, IC5.13 (-VCLAMP), IC5.14 (-VS), IC5.15 (-VS), IC5.16 (DGND), IC5.17 (EP), IC6.13 (-VCLAMP), IC6.14 (-VS), IC6.15 (-VS), IC6.16 (DGND), IC6.17 (EP), R6.2; also elsewhere on the board
CON_EXT_CH1+: CON_EXT_CH1+.S, RELAY1.7
CON_EXT_CH1-: CON_EXT_CH1-.S, RELAY1.2
CON_EXT_CH2+: CON_EXT_CH2+.S, RELAY2.7
CON_EXT_CH2-: CON_EXT_CH2-.S, RELAY2.2
CON_INT_CH1+: CON_INT_CH1+.S (SIG), RELAY1.5
CON_INT_CH1-: CON_INT_CH1-.S (SIG), RELAY1.4
CON_INT_CH2+: CON_INT_CH2+.S (SIG), RELAY2.5
CON_INT_CH2-: CON_INT_CH2-.S (SIG), RELAY2.4
FDA1_IN_N: R18.2, RELAY1.3, TP_FDA1_IN_N.P$1
FDA1_IN_P: R17.2, RELAY1.6, TP_FDA1_IN_P.P$1
FDA2_IN_N: R22.2, RELAY2.3, TP_FDA2_IN_N.P$1
FDA2_IN_P: R21.2, RELAY2.6, TP_FDA2_IN_P.P$1
unnamed: C32.1, R6.1, RELAY3.2, RELAY3.7
unnamed: IC6.10 (+OUT), R12.2
unnamed: IC5.10 (+OUT), R10.2
unnamed: IC5.11 (-OUT), R11.2
unnamed: IC6.11 (-OUT), R13.2
unnamed: C53.1, IC5.2 (+IN), R15.2, R17.1
unnamed: C53.2, IC5.1 (-FB), R15.1
unnamed: C54.1, IC5.4 (+FB), R16.1
unnamed: C54.2, IC5.3 (-IN), R16.2, R18.1
unnamed: C55.1, IC6.2 (+IN), R19.2, R21.1
unnamed: C55.2, IC6.1 (-FB), R19.1
unnamed: C56.2, IC6.3 (-IN), R20.2, R22.1
unnamed: C56.1, IC6.4 (+FB), R20.1
RD_OUT1: RELAY1.1; also elsewhere on the board
RD_OUT2: RELAY1.8; also elsewhere on the board
RD_OUT3: RELAY2.1; also elsewhere on the board
RD_OUT4: RELAY2.8; also elsewhere on the board
RD_OUT5: RELAY3.1; also elsewhere on the board
RD_OUT6: RELAY3.8; also elsewhere on the board
SHIELD: CON_EXT_CH1+.G1 (G), CON_EXT_CH1+.G2 (G), CON_EXT_CH1+.G3 (G), CON_EXT_CH1+.G4 (G), CON_EXT_CH1-.G1 (G), CON_EXT_CH1-.G2 (G), CON_EXT_CH1-.G3 (G), CON_EXT_CH1-.G4 (G), CON_EXT_CH2+.G1 (G), CON_EXT_CH2+.G2 (G), CON_EXT_CH2+.G3 (G), CON_EXT_CH2+.G4 (G), CON_EXT_CH2-.G1 (G), CON_EXT_CH2-.G2 (G), CON_EXT_CH2-.G3 (G), CON_EXT_CH2-.G4 (G), CON_INT_CH1+.G1 (GND), CON_INT_CH1+.G2 (GND), CON_INT_CH1-.G1 (GND), CON_INT_CH1-.G2 (GND), CON_INT_CH2+.G1 (GND), CON_INT_CH2+.G2 (GND), CON_INT_CH2-.G1 (GND), CON_INT_CH2-.G2 (GND), RELAY3.3, RELAY3.6; also elsewhere on the board
VCM: IC5.9 (VOCM), IC6.9 (VOCM), TP_VCM.P$1; also elsewhere on the board

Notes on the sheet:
ADC FRONTEND
pd, 2022
n.c.
R6 can be replaced with a 0 Ohm resistor to shorten SHIELD and GND.

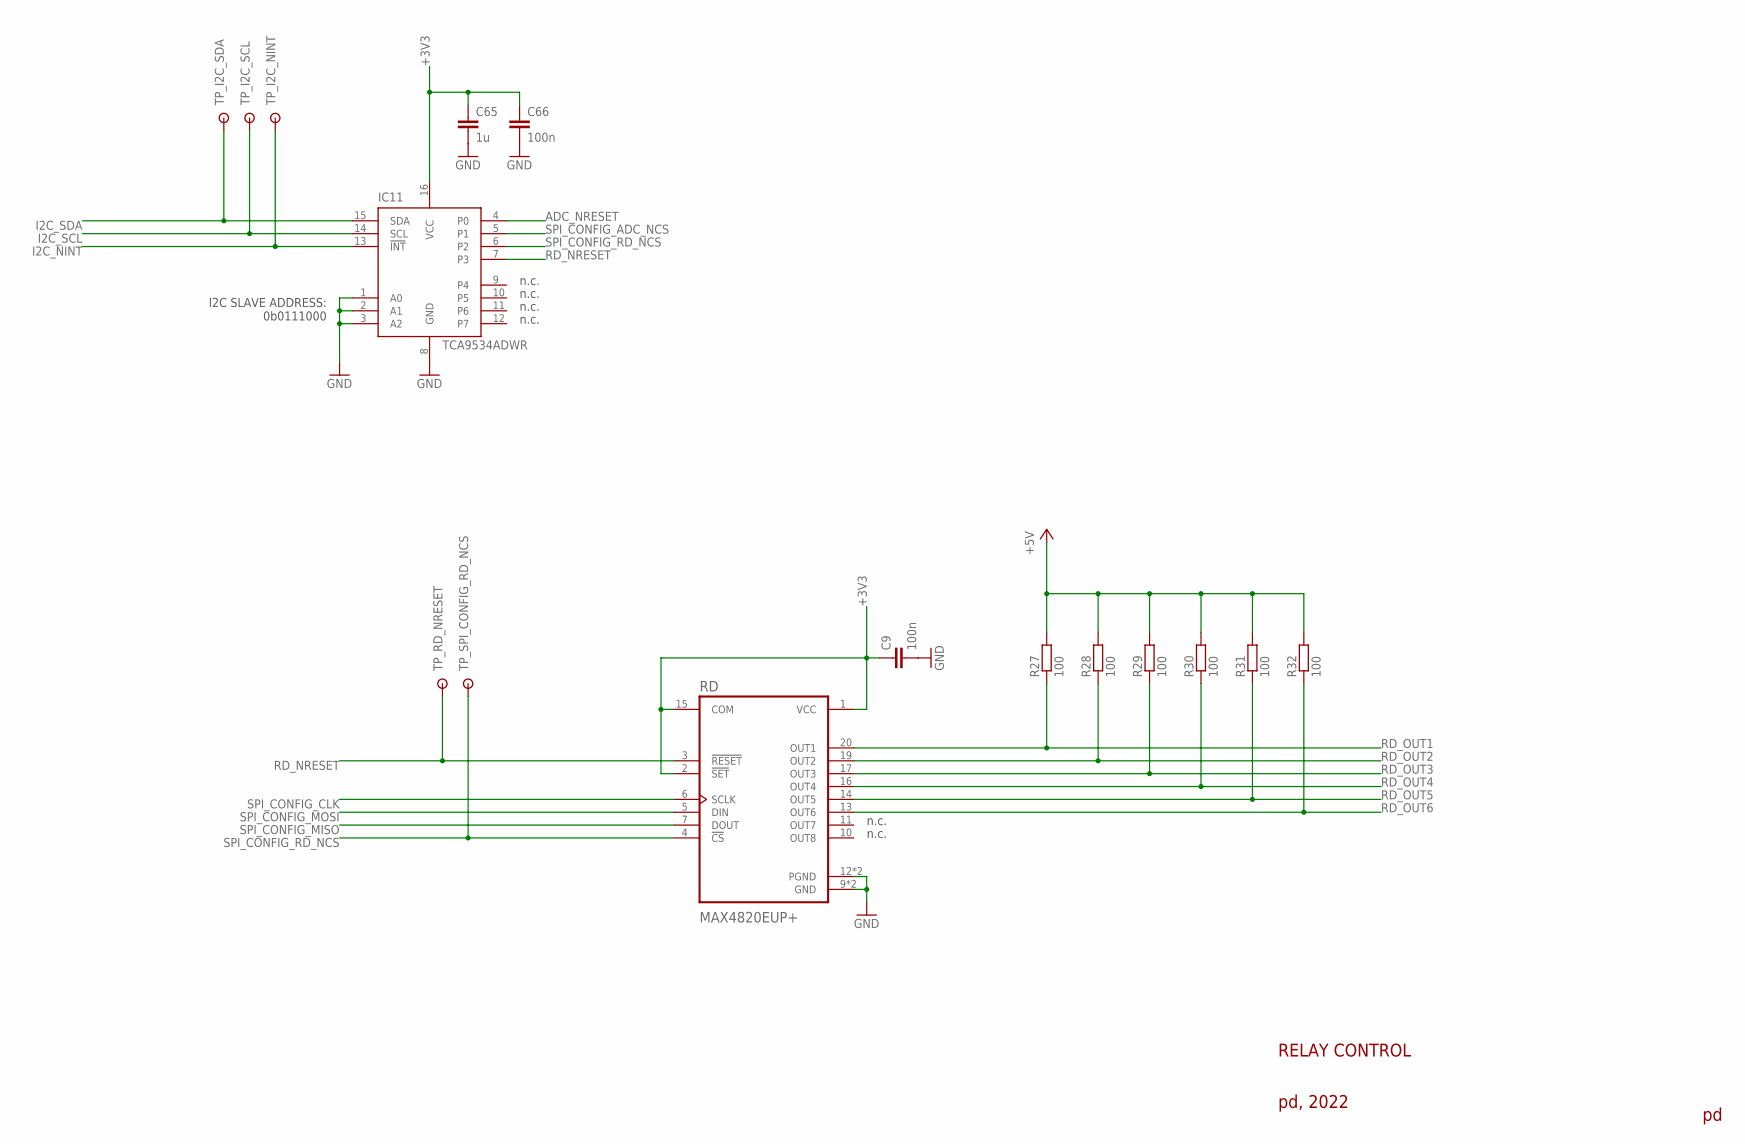
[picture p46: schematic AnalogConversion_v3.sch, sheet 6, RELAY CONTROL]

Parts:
C9, C66: 100n; C0603
C65: 1u; C0603
IC11: TCA9534ADWR
R27, R28, R29, R30, R31, R32: 100; R0603
RD: MAX4820EUP+
TP_I2C_NINT, TP_I2C_SCL, TP_I2C_SDA: RSPRO-1MM-TERMINAL-POST-2622034
TP_RD_NRESET: RSPRO-1MM-TERMINAL-POST-2622034
TP_SPI_CONFIG_RD_NCS: RSPRO-1MM-TERMINAL-POST-2622034

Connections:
+3V3: C9.1, C65.1, C66.1, IC11.16 (VCC), RD.1 (VCC), RD.2 (!SET), RD.15 (COM); also elsewhere on the board
+5V: R27.2, R28.2, R29.2, R30.2, R31.2, R32.2; also elsewhere on the board
ADC_NRESET: IC11.4 (P0); also elsewhere on the board
GND: C9.2, C65.2, C66.2, IC11.1 (A0), IC11.2 (A1), IC11.3 (A2), IC11.8 (GND), RD.9 (GND), RD.12 (PGND), RD.18 (PGND), RD.21 (GND); also elsewhere on the board
I2C_NINT: IC11.13 (!INT), TP_I2C_NINT.P$1; also elsewhere on the board
I2C_SCL: IC11.14 (SCL), TP_I2C_SCL.P$1; also elsewhere on the board
I2C_SDA: IC11.15 (SDA), TP_I2C_SDA.P$1; also elsewhere on the board
RD_NRESET: IC11.7 (P3), RD.3 (!RESET), TP_RD_NRESET.P$1
RD_OUT1: R27.1, RD.20 (OUT1); also elsewhere on the board
RD_OUT2: R28.1, RD.19 (OUT2); also elsewhere on the board
RD_OUT3: R29.1, RD.17 (OUT3); also elsewhere on the board
RD_OUT4: R30.1, RD.16 (OUT4); also elsewhere on the board
RD_OUT5: R31.1, RD.14 (OUT5); also elsewhere on the board
RD_OUT6: R32.1, RD.13 (OUT6); also elsewhere on the board
SPI_CONFIG_ADC_NCS: IC11.5 (P1); also elsewhere on the board
SPI_CONFIG_CLK: RD.6 (SCLK); also elsewhere on the board
SPI_CONFIG_MISO: RD.7 (DOUT); also elsewhere on the board
SPI_CONFIG_MOSI: RD.5 (DIN); also elsewhere on the board
SPI_CONFIG_RD_NCS: IC11.6 (P2), RD.4 (!CS), TP_SPI_CONFIG_RD_NCS.P$1

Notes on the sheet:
RELAY CONTROL
pd, 2022
n.c.
I2C SLAVE ADDRESS: 0b0111000

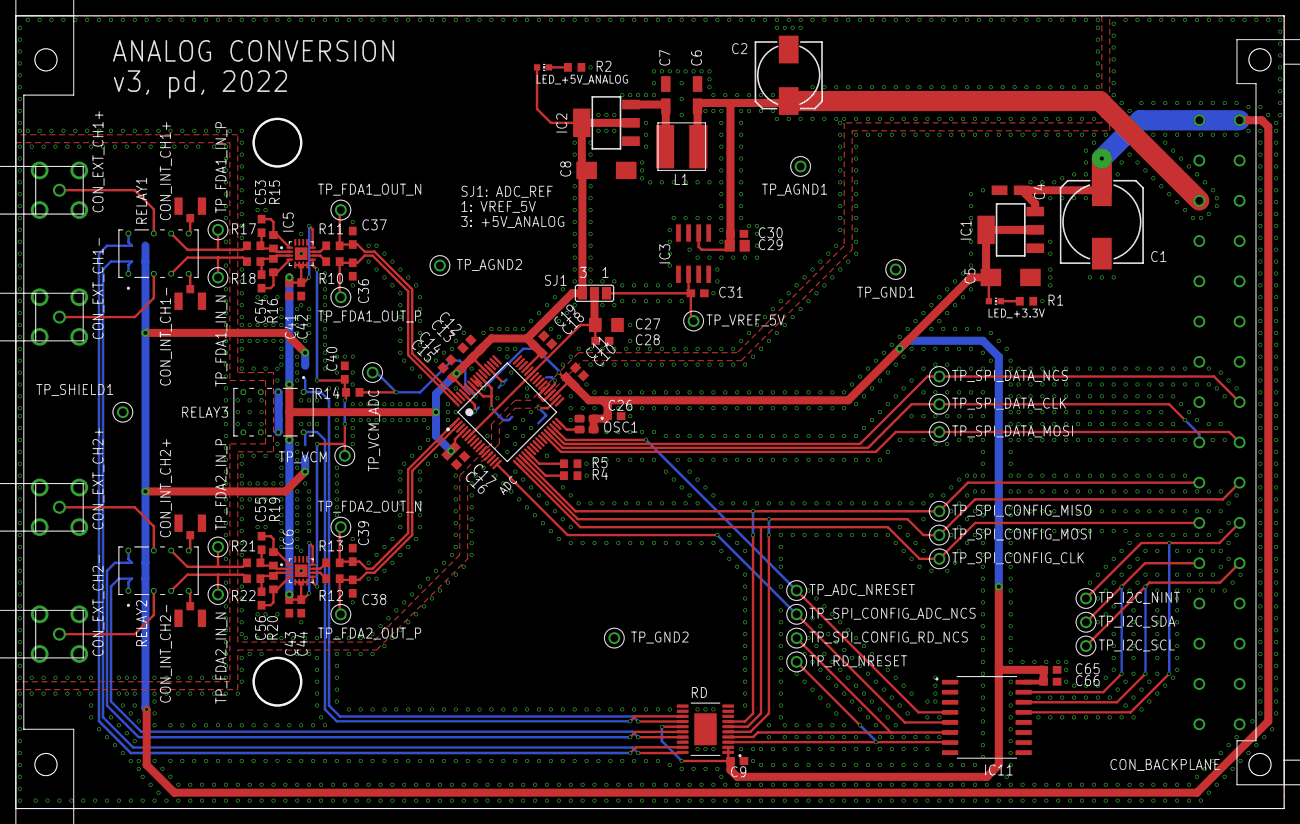
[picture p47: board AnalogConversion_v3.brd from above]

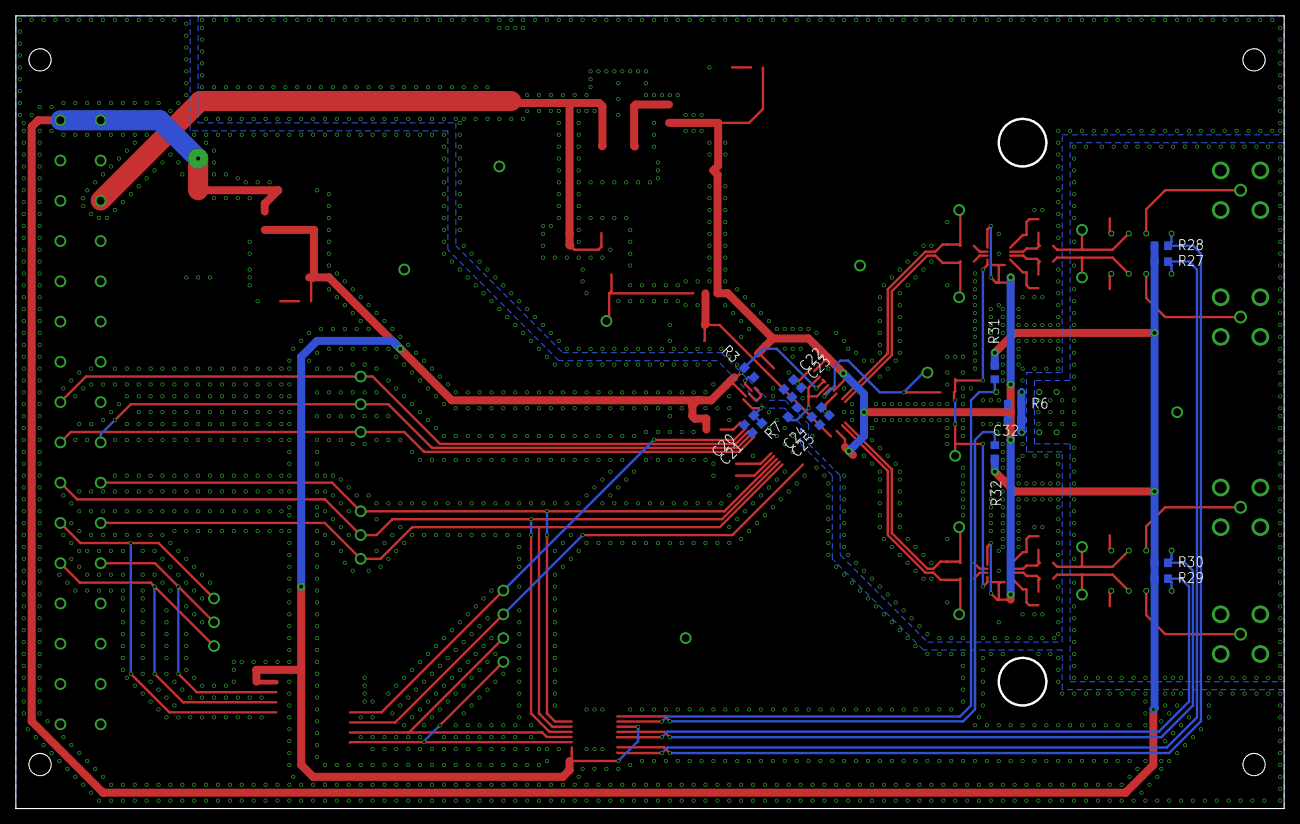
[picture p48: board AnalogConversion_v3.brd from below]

Board: 2 copper layers, 160.0 x 100.0 mm, 127 parts (16 on the bottom side), 70 nets.

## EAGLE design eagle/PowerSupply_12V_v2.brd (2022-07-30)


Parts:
PCB_BRACKET: 60807-011

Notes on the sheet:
POWER SUPPLY +/-12 V
pd, 2022
github.com/yildi1337
SHEET ORDER: 02: DIN 41612 CONNECTOR 03: POWER SUPPLY +/-12 V


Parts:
CON_BACKPLANE: 09031326921
TP_GND1, TP_GND2: RSPRO-1MM-TERMINAL-POST-2622034

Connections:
+5V: CON_BACKPLANE.1, CON_BACKPLANE.2
+12V: CON_BACKPLANE.5; also elsewhere on the board
-12V: CON_BACKPLANE.6; also elsewhere on the board
BITE_PS_5V_TS1: CON_BACKPLANE.11
BITE_PS_5V_TS2: CON_BACKPLANE.12
BITE_PS_12V_TS1: CON_BACKPLANE.13
BITE_PS_12V_TS2: CON_BACKPLANE.14
BITE_PS_+5V_CURRENT: CON_BACKPLANE.9
GND: CON_BACKPLANE.3, CON_BACKPLANE.4, CON_BACKPLANE.7, CON_BACKPLANE.8, CON_BACKPLANE.10, CON_BACKPLANE.15, CON_BACKPLANE.16, CON_BACKPLANE.17, CON_BACKPLANE.18, CON_BACKPLANE.19, CON_BACKPLANE.20, CON_BACKPLANE.21, CON_BACKPLANE.22, CON_BACKPLANE.23, CON_BACKPLANE.24, CON_BACKPLANE.29, CON_BACKPLANE.30, CON_BACKPLANE.31, CON_BACKPLANE.32, TP_GND1.P$1, TP_GND2.P$1; also elsewhere on the board
L: CON_BACKPLANE.27, CON_BACKPLANE.28; also elsewhere on the board
N: CON_BACKPLANE.25, CON_BACKPLANE.26; also elsewhere on the board

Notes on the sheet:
DIN 41612 CONNECTOR
pd, 2022
github.com/yildi1337


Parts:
C1, C2, C6, C7: 22u/25V; 153CLV-0505
C3, C5, C8, C10: 100n; C0603
C4, C9: 100u/25V; 153CLV-0810
FUSE_+12V: 0031.8201
FUSE_-12V: 0031.8201
HS1, HS2: FK 237 SA 220 O; FK_237_SA_220_O
IC1: L7812CV
IC2: L7912CV
L1, L2: VLS6045AF-101M
LED_+12V_OK: 113-314-04
LED_-12V_OK: 113-314-04
PS1, PS2: TMLM_20115; TMLM_201XX
R1, R2: 680; R0603
TP_+12V: RSPRO-1MM-TERMINAL-POST-2622034
TP_-12V: RSPRO-1MM-TERMINAL-POST-2622034

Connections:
+12V: FUSE_+12V.2, R1.2; also elsewhere on the board
-12V: FUSE_-12V.2, R2.1; also elsewhere on the board
GND: C1.-, C2.-, C3.2, C4.-, C5.2, C6.+, C7.+, C8.1, C9.+, C10.1, IC1.2 (GND), IC2.1 (GND), LED_+12V_OK.- (C), LED_-12V_OK.+ (A), PS1.3 (-VOUT), PS2.2 (+VOUT); also elsewhere on the board
L: PS1.5 (AC(L)), PS2.5 (AC(L)); also elsewhere on the board
N: PS1.6 (AC(N)), PS2.6 (AC(N)); also elsewhere on the board
unnamed: C7.-, C8.2, IC2.2 (IN), L2.1
unnamed: LED_-12V_OK.- (C), R2.2
unnamed: C9.-, C10.2, FUSE_-12V.1, IC2.3 (OUT), TP_-12V.P$1
unnamed: C1.+, L1.1, PS1.2 (+VOUT)
unnamed: C6.-, L2.2, PS2.3 (-VOUT)
unnamed: LED_+12V_OK.+ (A), R1.1
unnamed: C4.+, C5.1, FUSE_+12V.1, IC1.3 (OUT), TP_+12V.P$1
unnamed: C2.+, C3.1, IC1.1 (IN), L1.2

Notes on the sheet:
POWER SUPPLY +/-12 V
pd, 2022
github.com/yildi1337


Board: 2 copper layers, 160.0 x 100.0 mm, 30 parts (0 on the bottom side), 14 nets.

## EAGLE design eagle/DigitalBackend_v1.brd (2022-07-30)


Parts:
PCB_BRACKET: 60807-011

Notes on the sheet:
DIGITAL BACKEND
pd, 2022
github.com/yildi1337
SHEET ORDER: 02: DIN 41612 CONNECTOR 03: VOLTAGE REGULATORS 04: MCU 05: USB PHY 06: DEBUG


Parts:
C1: 1000u/16V; 153CLV-1010
C2, C3: 100u/25V; 153CLV-0810
CON_BACKPLANE: 09031326921
TP_GND1, TP_GND2, TP_GND3, TP_GND4: RSPRO-1MM-TERMINAL-POST-2622034

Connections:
+3V3_VDD: CON_BACKPLANE.27; also elsewhere on the board
+5V: C1.+, CON_BACKPLANE.1, CON_BACKPLANE.2; also elsewhere on the board
+12V: C2.+, CON_BACKPLANE.5; also elsewhere on the board
-12V: C3.-, CON_BACKPLANE.6
BITE_PS_5V_TS1: CON_BACKPLANE.11
BITE_PS_5V_TS2: CON_BACKPLANE.12
BITE_PS_12V_TS1: CON_BACKPLANE.13
BITE_PS_12V_TS2: CON_BACKPLANE.14
BITE_PS_+5V_CURRENT: CON_BACKPLANE.9
GND: C1.-, C2.-, C3.+, CON_BACKPLANE.3, CON_BACKPLANE.4, CON_BACKPLANE.7, CON_BACKPLANE.8, CON_BACKPLANE.10, CON_BACKPLANE.15, CON_BACKPLANE.31, CON_BACKPLANE.32, TP_GND1.P$1, TP_GND2.P$1, TP_GND3.P$1, TP_GND4.P$1; also elsewhere on the board
I2C4_NINT: CON_BACKPLANE.22; also elsewhere on the board
I2C4_SCL: CON_BACKPLANE.24; also elsewhere on the board
I2C4_SDA: CON_BACKPLANE.23; also elsewhere on the board
SPI2_MOSI: CON_BACKPLANE.18; also elsewhere on the board
SPI2_NSS: CON_BACKPLANE.16; also elsewhere on the board
SPI2_SCK: CON_BACKPLANE.17; also elsewhere on the board
SPI3_MISO: CON_BACKPLANE.19; also elsewhere on the board
SPI3_MOSI: CON_BACKPLANE.20; also elsewhere on the board
SPI3_SCK: CON_BACKPLANE.21; also elsewhere on the board
USART1_RX: CON_BACKPLANE.25; also elsewhere on the board
USART1_TX: CON_BACKPLANE.26; also elsewhere on the board
USB_DATA_DM: CON_BACKPLANE.30; also elsewhere on the board
USB_DATA_DP: CON_BACKPLANE.29; also elsewhere on the board
VBUS_USB_DATA: CON_BACKPLANE.28; also elsewhere on the board

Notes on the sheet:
DIN 41612 CONNECTOR
pd, 2022
github.com/yildi1337


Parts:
C4, C6, C7: 10u; CT3216
C5, C8: 22u; CT6032
IC1, IC2: LM1117IMP-3.3; SOT223
L1: 100u; VLS6045AF-101M
LED_+3.3V_VDD, LED_+3V3_VDDA: LEDCHIP-LED0603; CHIP-LED0603
R1, R2: 750; R0603

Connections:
+3V3_VDD: C5.+, IC1.2 (OUT), IC1.TAB (OUT1), LED_+3.3V_VDD.A; also elsewhere on the board
+3V3_VDDA: C8.+, IC2.2 (OUT), IC2.TAB (OUT1), LED_+3V3_VDDA.A; also elsewhere on the board
+5V: C4.+, IC1.3 (IN); also elsewhere on the board
+12V: C6.+, L1.1; also elsewhere on the board
GND: C4.-, C5.-, C6.-, C7.-, C8.-, IC1.1 (GND), IC2.1 (GND), R1.2, R2.2; also elsewhere on the board
unnamed: C7.+, IC2.3 (IN), L1.2
unnamed: LED_+3.3V_VDD.C, R1.1
unnamed: LED_+3V3_VDDA.C, R2.1

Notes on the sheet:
VOLTAGE REGULATORS
pd, 2022
github.com/yildi1337
Green: 2 mA / 1.9 V

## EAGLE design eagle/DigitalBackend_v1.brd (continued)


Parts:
C11, C12, C27: 1u; C0603
C13, C16, C17, C18, C19, C20, C21, C22, C23, C24, C25, C26, C28: 100n; C0603
C29: 4.7u; C0603
C30, C31: 2.2u; C0603
C43, C44: 5.6p; C0603
C45, C46: 15p; C0603
MCU: STM32H753ZIT6; LQFP144
R3, R4: 10k; R0603
R8, R9, R10: 1.5k; R0603
SJ1: SJ2W; SJ_2
XTAL1: XRCGB25M000F2P00R0
XTAL2: ABS05-32.768KHZ-T

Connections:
+3V3_VDD: C11.1, C16.1, C17.1, C18.1, C19.1, C20.1, C21.1, C22.1, C23.1, C24.1, C25.1, C26.1, C27.1, C28.1, C29.1, MCU.6 (VBAT), MCU.17 (VDD), MCU.30 (VDD), MCU.39 (VDD), MCU.52 (VDD), MCU.62 (VDD), MCU.72 (VDD), MCU.84 (VDD), MCU.95 (VDD33USB), MCU.108 (VDD), MCU.121 (VDD), MCU.131 (VDD), MCU.144 (VDD), R3.2, R8.2, R9.2, R10.2, SJ1.3; also elsewhere on the board
+3V3_VDDA: C12.1, C13.1, MCU.32 (VREF+), MCU.33 (VDDA); also elsewhere on the board
DEBUG1: MCU.63 (PE10); also elsewhere on the board
DEBUG2: MCU.64 (PE11); also elsewhere on the board
DEBUG3: MCU.65 (PE12); also elsewhere on the board
DEBUG4: MCU.66 (PE13); also elsewhere on the board
GND: C11.2, C12.2, C13.2, C16.2, C17.2, C18.2, C19.2, C20.2, C21.2, C22.2, C23.2, C24.2, C25.2, C26.2, C27.2, C28.2, C29.2, C30.2, C31.2, C43.2, C44.2, C45.2, C46.2, MCU.16 (VSS), MCU.31 (VSSA), MCU.38 (VSS), MCU.51 (VSS), MCU.61 (VSS), MCU.83 (VSS), MCU.94 (VSS), MCU.107 (VSS), MCU.120 (VSS), MCU.130 (VSS), SJ1.1, XTAL1.2 (GND2), XTAL1.4 (GND4); also elsewhere on the board
I2C4_NINT: MCU.87 (PG2), R10.1; also elsewhere on the board
I2C4_SCL: MCU.81 (PD12), R8.1; also elsewhere on the board
I2C4_SDA: MCU.82 (PD13), R9.1; also elsewhere on the board
JTCK/SWCLK: MCU.109 (PA14); also elsewhere on the board
JTDI: MCU.110 (PA15); also elsewhere on the board
JTDO/TRACESWO: MCU.133 (PB3); also elsewhere on the board
JTMS/SWDIO: MCU.105 (PA13); also elsewhere on the board
LED1: MCU.1 (PE2); also elsewhere on the board
LED2: MCU.2 (PE3); also elsewhere on the board
LED3: MCU.3 (PE4); also elsewhere on the board
LED4: MCU.4 (PE5); also elsewhere on the board
unnamed: MCU.143 (PDR_ON), R3.1
unnamed: MCU.138 (BOOT0), R4.2
unnamed: R4.1, SJ1.2
unnamed: C45.1, MCU.8 (PC14-OSC32_IN), XTAL2.1
unnamed: C44.1, MCU.23 (PH0-OSC_IN), XTAL1.3
unnamed: C43.1, MCU.24 (PH1-OSC_OUT), XTAL1.1
unnamed: C46.1, MCU.9 (PC15-OSC32_OUT), XTAL2.2
NJTRST: MCU.134 (PB4); also elsewhere on the board
NRST: MCU.25 (NRST); also elsewhere on the board
SPI2_MOSI: MCU.76 (PB15); also elsewhere on the board
SPI2_NSS: MCU.140 (PB9); also elsewhere on the board
SPI2_SCK: MCU.117 (PD3); also elsewhere on the board
SPI3_MISO: MCU.112 (PC11); also elsewhere on the board
SPI3_MOSI: MCU.122 (PD6); also elsewhere on the board
SPI3_SCK: MCU.111 (PC10); also elsewhere on the board
ULPI_CLK: MCU.41 (PA5); also elsewhere on the board
ULPI_DATA0: MCU.37 (PA3); also elsewhere on the board
ULPI_DATA1: MCU.46 (PB0); also elsewhere on the board
ULPI_DATA2: MCU.47 (PB1); also elsewhere on the board
ULPI_DATA3: MCU.69 (PB10); also elsewhere on the board
ULPI_DATA4: MCU.70 (PB11); also elsewhere on the board
ULPI_DATA5: MCU.73 (PB12); also elsewhere on the board
ULPI_DATA6: MCU.74 (PB13); also elsewhere on the board
ULPI_DATA7: MCU.135 (PB5); also elsewhere on the board
ULPI_DIR: MCU.28 (PC2_C); also elsewhere on the board
ULPI_NXT: MCU.29 (PC3_C); also elsewhere on the board
ULPI_STP: MCU.26 (PC0); also elsewhere on the board
USART1_RX: MCU.137 (PB7); also elsewhere on the board
USART1_TX: MCU.136 (PB6); also elsewhere on the board
VCAP: C30.1, C31.1, MCU.71 (VCAP), MCU.106 (VCAP)

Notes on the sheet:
MCU
pd, 2022
github.com/yildi1337
ESR < 1 Ohm
Power supply supervisor enabled
Boot from user flash
Boot from system flash
VBAT
VDDA
VDD33USB
VREF+


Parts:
C33, C34, C35, C36, C37, C40: 100n; C0603
C38, C39: 4.7u; C0603
C41, C42: 27p; C0603
IC4: USB3300-EZK
R15: 2k; R0603
R16: 10k; R0603
R17: 1M; R0603
R18: 820; R0603
R19: 4.7k; R0603
XTAL3: FOXSDLF-240F-20

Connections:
+3V3_VDD: C33.1, C34.1, C35.1, C36.1, IC4.6 (VDD3.3-3), IC4.16 (VDD3.3-2), IC4.25 (VDD3.3-1), IC4.30 (VDD3.3), IC4.31 (REG_EN); also elsewhere on the board
GND: C33.2, C34.2, C35.2, C36.2, C37.2, C38.2, C39.2, C40.2, C41.2, C42.2, IC4.1 (GND-1), IC4.2 (GND), IC4.33 (EXP), R16.1, R19.1; also elsewhere on the board
unnamed: C37.1, C38.1, IC4.15 (VDD1.8-1), IC4.26 (VDD1.8)
unnamed: C39.1, C40.1, IC4.29 (VDDA1.8)
unnamed: R15.1, R16.2
unnamed: IC4.32 (RBIAS), R15.2
unnamed: C41.1, IC4.27 (XO), R17.2, XTAL3.1
unnamed: C42.1, IC4.28 (XI), R17.1, XTAL3.2
unnamed: IC4.4 (VBUS), R18.1
unnamed: IC4.9 (RESET), R19.2
ULPI_CLK: IC4.14 (CLKOUT); also elsewhere on the board
ULPI_DATA0: IC4.24 (DATA[0]); also elsewhere on the board
ULPI_DATA1: IC4.23 (DATA[1]); also elsewhere on the board
ULPI_DATA2: IC4.22 (DATA[2]); also elsewhere on the board
ULPI_DATA3: IC4.21 (DATA[3]); also elsewhere on the board
ULPI_DATA4: IC4.20 (DATA[4]); also elsewhere on the board
ULPI_DATA5: IC4.19 (DATA[5]); also elsewhere on the board
ULPI_DATA6: IC4.18 (DATA[6]); also elsewhere on the board
ULPI_DATA7: IC4.17 (DATA[7]); also elsewhere on the board
ULPI_DIR: IC4.12 (DIR); also elsewhere on the board
ULPI_NXT: IC4.11 (NXT); also elsewhere on the board
ULPI_STP: IC4.13 (STP); also elsewhere on the board
USB_DATA_DM: IC4.8 (DM); also elsewhere on the board
USB_DATA_DP: IC4.7 (DP); also elsewhere on the board
VBUS_USB_DATA: R18.2; also elsewhere on the board

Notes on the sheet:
USB PHY
pd, 2022
n.c.
Next to pin 26
Next to pin 15
Next to pin 29


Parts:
C32, C93: 100n; C0603
CON_JTAG: TST-110-01-T-DJ; TST-110-01-T-D
IC5: 74LVC126AD,112; SO14
LED1, LED2, LED3, LED4: 113-314-04
LED_DEBUG1, LED_DEBUG2, LED_DEBUG3, LED_DEBUG4: LEDCHIP-LED0603; CHIP-LED0603
R5, R6, R7: 10k; R0603
R60, R61, R62, R63: 68; R0603
R64, R65, R66, R67: 750; R0603
SW_RST_MCU: TP33W008000
TP_DEBUG1, TP_DEBUG2, TP_DEBUG3, TP_DEBUG4: RSPRO-1MM-TERMINAL-POST-2622034

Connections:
+3V3_VDD: C93.2, CON_JTAG.1, CON_JTAG.2, IC5.1 (OE), IC5.4 (OE), IC5.10 (OE), IC5.13 (OE), IC5.14 (VCC); also elsewhere on the board
DEBUG1: LED_DEBUG1.A, TP_DEBUG1.P$1; also elsewhere on the board
DEBUG2: LED_DEBUG2.A, TP_DEBUG2.P$1; also elsewhere on the board
DEBUG3: LED_DEBUG3.A, TP_DEBUG3.P$1; also elsewhere on the board
DEBUG4: LED_DEBUG4.A, TP_DEBUG4.P$1; also elsewhere on the board
GND: C32.1, C93.1, CON_JTAG.4, CON_JTAG.6, CON_JTAG.8, CON_JTAG.10, CON_JTAG.12, CON_JTAG.14, CON_JTAG.16, CON_JTAG.18, CON_JTAG.20, IC5.7 (GND), LED1.- (C), LED2.- (C), LED3.- (C), LED4.- (C), R5.1, R6.1, R7.1, R64.2, R65.2, R66.2, R67.2, SW_RST_MCU.GND1, SW_RST_MCU.GND2, SW_RST_MCU.P1; also elsewhere on the board
JTCK/SWCLK: CON_JTAG.9; also elsewhere on the board
JTDI: CON_JTAG.5; also elsewhere on the board
JTDO/TRACESWO: CON_JTAG.13; also elsewhere on the board
JTMS/SWDIO: CON_JTAG.7; also elsewhere on the board
LED1: IC5.2 (I); also elsewhere on the board
LED2: IC5.5 (I); also elsewhere on the board
LED3: IC5.9 (I); also elsewhere on the board
LED4: IC5.12 (I); also elsewhere on the board
unnamed: CON_JTAG.19, R7.2
unnamed: CON_JTAG.17, R6.2
unnamed: CON_JTAG.11, R5.2
unnamed: LED1.+ (A), R60.2
unnamed: LED2.+ (A), R61.2
unnamed: LED3.+ (A), R62.2
unnamed: LED4.+ (A), R63.2
unnamed: IC5.3 (O), R60.1
unnamed: IC5.6 (O), R61.1
unnamed: IC5.8 (O), R62.1
unnamed: IC5.11 (O), R63.1
unnamed: LED_DEBUG1.C, R64.1
unnamed: LED_DEBUG2.C, R65.1
unnamed: LED_DEBUG3.C, R66.1
unnamed: LED_DEBUG4.C, R67.1
NJTRST: CON_JTAG.3; also elsewhere on the board
NRST: C32.2, CON_JTAG.15, SW_RST_MCU.P3; also elsewhere on the board

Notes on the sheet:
DEBUG
pd, 2022
Yellow: 2 mA / 1.85 V



Board: 2 copper layers, 160.0 x 100.0 mm, 98 parts (17 on the bottom side), 80 nets.

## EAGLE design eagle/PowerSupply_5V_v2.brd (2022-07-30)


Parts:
PCB_BRACKET: 60807-011

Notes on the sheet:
POWER SUPPLY +5 V
pd, 2022
github.com/yildi1337
SHEET ORDER: 02: DIN 41612 CONNECTOR 03: POWER SUPPLY +5 V


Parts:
CON_BACKPLANE: 09031326921
TP_GND1, TP_GND2: RSPRO-1MM-TERMINAL-POST-2622034

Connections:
+5V: CON_BACKPLANE.1, CON_BACKPLANE.2; also elsewhere on the board
+12V: CON_BACKPLANE.5
-12V: CON_BACKPLANE.6
BITE_PS_5V_TS1: CON_BACKPLANE.11
BITE_PS_5V_TS2: CON_BACKPLANE.12
BITE_PS_12V_TS1: CON_BACKPLANE.13
BITE_PS_12V_TS2: CON_BACKPLANE.14
BITE_PS_+5V_CURRENT: CON_BACKPLANE.9
GND: CON_BACKPLANE.3, CON_BACKPLANE.4, CON_BACKPLANE.7, CON_BACKPLANE.8, CON_BACKPLANE.10, CON_BACKPLANE.15, CON_BACKPLANE.16, CON_BACKPLANE.17, CON_BACKPLANE.18, CON_BACKPLANE.19, CON_BACKPLANE.20, CON_BACKPLANE.21, CON_BACKPLANE.22, CON_BACKPLANE.23, CON_BACKPLANE.24, CON_BACKPLANE.29, CON_BACKPLANE.30, CON_BACKPLANE.31, CON_BACKPLANE.32, TP_GND1.P$1, TP_GND2.P$1; also elsewhere on the board
L: CON_BACKPLANE.27, CON_BACKPLANE.28; also elsewhere on the board
N: CON_BACKPLANE.25, CON_BACKPLANE.26; also elsewhere on the board

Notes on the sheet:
DIN 41612 CONNECTOR
pd, 2022
github.com/yildi1337


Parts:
C1: 47u/16V; 153CLV-0505
C2: 100n; C0603
FUSE_+5V: 0031.8201
LED_+5V_OK: 113-314-04
PS1: TMLM_20105; TMLM_201XX
R1: 150; R0603

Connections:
+5V: FUSE_+5V.2, R1.2; also elsewhere on the board
GND: C1.-, C2.2, LED_+5V_OK.- (C), PS1.3 (-VOUT); also elsewhere on the board
L: PS1.5 (AC(L)); also elsewhere on the board
N: PS1.6 (AC(N)); also elsewhere on the board
unnamed: C1.+, C2.1, FUSE_+5V.1, PS1.2 (+VOUT)
unnamed: LED_+5V_OK.+ (A), R1.1

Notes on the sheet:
POWER SUPPLY +5 V
pd, 2022
github.com/yildi1337


Board: 2 copper layers, 160.0 x 100.0 mm, 10 parts (0 on the bottom side), 6 nets.

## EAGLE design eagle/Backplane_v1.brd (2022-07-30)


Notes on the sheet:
BACKPLANE
pd, 2022
github.com/yildi1337
SHEET ORDER: 02: DIN 41612 CONNECTORS 03: TESTPINS

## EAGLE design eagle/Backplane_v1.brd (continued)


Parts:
C+5V_1, C+5V_2, C+5V_3, C+5V_4, C+5V_5, C+5V_6, C+5V_7, C+12V_1, C+12V_2, C+12V_3, C+12V_4, C+12V_5, C+12V_6, C+12V_7: 100n; C0603
C-12V_1, C-12V_2, C-12V_3, C-12V_4, C-12V_5, C-12V_6, C-12V_7: 100n; C0603
CON_ACNV: 09032326825
CON_AFE: 09032326825
CON_CAL: 09032326825
CON_DBE: 09032326825
CON_L: 63824-1
CON_N: 63824-1
CON_PE: 63824-1
CON_PS_5V, CON_PS_12V: 09032326825
CON_USB: TST-105-01-T-D
TP_GND1, TP_GND2, TP_GND3, TP_GND4, TP_GND5, TP_GND6: RSPRO-1MM-TERMINAL-POST-2622034

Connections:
+3V3_MCU: CON_DBE.27, CON_USB.8; also elsewhere on the board
+5V: C+5V_1.1, C+5V_2.1, C+5V_3.1, C+5V_4.1, C+5V_5.1, C+5V_6.1, C+5V_7.1, CON_ACNV.1, CON_ACNV.2, CON_AFE.1, CON_AFE.2, CON_CAL.1, CON_CAL.2, CON_DBE.1, CON_DBE.2, CON_PS_5V.1, CON_PS_5V.2, CON_PS_12V.1, CON_PS_12V.2; also elsewhere on the board
+12V: C+12V_1.1, C+12V_2.1, C+12V_3.1, C+12V_4.1, C+12V_5.1, C+12V_6.1, C+12V_7.1, CON_ACNV.5, CON_AFE.5, CON_CAL.5, CON_DBE.5, CON_PS_5V.5, CON_PS_12V.5; also elsewhere on the board
-12V: C-12V_1.1, C-12V_2.1, C-12V_3.1, C-12V_4.1, C-12V_5.1, C-12V_6.1, C-12V_7.1, CON_ACNV.6, CON_AFE.6, CON_CAL.6, CON_DBE.6, CON_PS_5V.6, CON_PS_12V.6; also elsewhere on the board
BITE_PS_5V_TS1: CON_ACNV.11, CON_AFE.11, CON_CAL.11, CON_DBE.11, CON_PS_5V.11, CON_PS_12V.11; also elsewhere on the board
BITE_PS_5V_TS2: CON_ACNV.12, CON_AFE.12, CON_CAL.12, CON_DBE.12, CON_PS_5V.12, CON_PS_12V.12; also elsewhere on the board
BITE_PS_12V_TS1: CON_ACNV.13, CON_AFE.13, CON_CAL.13, CON_DBE.13, CON_PS_5V.13, CON_PS_12V.13; also elsewhere on the board
BITE_PS_12V_TS2: CON_ACNV.14, CON_AFE.14, CON_CAL.14, CON_DBE.14, CON_PS_5V.14, CON_PS_12V.14; also elsewhere on the board
BITE_PS_+5V_CURRENT: CON_ACNV.9, CON_AFE.9, CON_CAL.9, CON_DBE.9, CON_PS_5V.9, CON_PS_12V.9; also elsewhere on the board
GND: C+5V_1.2, C+5V_2.2, C+5V_3.2, C+5V_4.2, C+5V_5.2, C+5V_6.2, C+5V_7.2, C+12V_1.2, C+12V_2.2, C+12V_3.2, C+12V_4.2, C+12V_5.2, C+12V_6.2, C+12V_7.2, C-12V_1.2, C-12V_2.2, C-12V_3.2, C-12V_4.2, C-12V_5.2, C-12V_6.2, C-12V_7.2, CON_ACNV.3, CON_ACNV.4, CON_ACNV.7, CON_ACNV.8, CON_ACNV.10, CON_ACNV.15, CON_ACNV.25, CON_ACNV.26, CON_ACNV.27, CON_ACNV.28, CON_ACNV.29, CON_ACNV.30, CON_ACNV.31, CON_ACNV.32, CON_AFE.3, CON_AFE.4, CON_AFE.7, CON_AFE.8, CON_AFE.10, CON_AFE.15, CON_AFE.16, CON_AFE.17, CON_AFE.18, CON_AFE.25, CON_AFE.26, CON_AFE.27, CON_AFE.28, CON_AFE.29, CON_AFE.30, CON_AFE.31, CON_AFE.32, CON_CAL.3, CON_CAL.4, CON_CAL.7, CON_CAL.8, CON_CAL.10, CON_CAL.15, CON_CAL.16, CON_CAL.17, CON_CAL.18, CON_CAL.25, CON_CAL.26, CON_CAL.27, CON_CAL.28, CON_CAL.29, CON_CAL.30, CON_CAL.31, CON_CAL.32, CON_DBE.3, CON_DBE.4, CON_DBE.7, CON_DBE.8, CON_DBE.10, CON_DBE.15, CON_DBE.31, CON_DBE.32, CON_PE.1, CON_PE.2, CON_PS_5V.3, CON_PS_5V.4, CON_PS_5V.7, CON_PS_5V.8, CON_PS_5V.10, CON_PS_5V.15, CON_PS_5V.16, CON_PS_5V.17, CON_PS_5V.18, CON_PS_5V.19, CON_PS_5V.20, CON_PS_5V.21, CON_PS_5V.22, CON_PS_5V.23, CON_PS_5V.24, CON_PS_5V.29, CON_PS_5V.30, CON_PS_5V.31, CON_PS_5V.32, CON_PS_12V.3, CON_PS_12V.4, CON_PS_12V.7, CON_PS_12V.8, CON_PS_12V.10, CON_PS_12V.15, CON_PS_12V.16, CON_PS_12V.17, CON_PS_12V.18, CON_PS_12V.19, CON_PS_12V.20, CON_PS_12V.21, CON_PS_12V.22, CON_PS_12V.23, CON_PS_12V.24, CON_PS_12V.29, CON_PS_12V.30, CON_PS_12V.31, CON_PS_12V.32, CON_USB.4, CON_USB.5, CON_USB.6, CON_USB.7, TP_GND1.P$1, TP_GND2.P$1, TP_GND3.P$1, TP_GND4.P$1, TP_GND5.P$1, TP_GND6.P$1
I2C_NINT: CON_ACNV.22, CON_AFE.22, CON_CAL.22, CON_DBE.22; also elsewhere on the board
I2C_SCL: CON_ACNV.24, CON_AFE.24, CON_CAL.24, CON_DBE.24; also elsewhere on the board
I2C_SDA: CON_ACNV.23, CON_AFE.23, CON_CAL.23, CON_DBE.23; also elsewhere on the board
L: CON_L.1, CON_L.2, CON_PS_5V.27, CON_PS_5V.28, CON_PS_12V.27, CON_PS_12V.28
N: CON_N.1, CON_N.2, CON_PS_5V.25, CON_PS_5V.26, CON_PS_12V.25, CON_PS_12V.26
SPI_CONFIG_CLK: CON_ACNV.21, CON_AFE.21, CON_CAL.21, CON_DBE.21; also elsewhere on the board
SPI_CONFIG_MISO: CON_ACNV.19, CON_AFE.19, CON_CAL.19, CON_DBE.19; also elsewhere on the board
SPI_CONFIG_MOSI: CON_ACNV.20, CON_AFE.20, CON_CAL.20, CON_DBE.20; also elsewhere on the board
SPI_DATA_CLK: CON_ACNV.17, CON_DBE.17; also elsewhere on the board
SPI_DATA_MOSI: CON_ACNV.18, CON_DBE.18; also elsewhere on the board
SPI_DATA_NCS: CON_ACNV.16, CON_DBE.16; also elsewhere on the board
USART_RX: CON_DBE.25, CON_USB.10; also elsewhere on the board
USART_TX: CON_DBE.26, CON_USB.9; also elsewhere on the board
USB_DATA_DM: CON_DBE.30, CON_USB.1; also elsewhere on the board
USB_DATA_DP: CON_DBE.29, CON_USB.2; also elsewhere on the board
VBUS_USB_DATA: CON_DBE.28, CON_USB.3; also elsewhere on the board

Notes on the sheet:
DIN 41612 CONNECTORS
pd, 2022
github.com/yildi1337


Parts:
TP_+3V3_MCU, TP_+5V, TP_+12V: RSPRO-1MM-TERMINAL-POST-2622034
TP_-12V: RSPRO-1MM-TERMINAL-POST-2622034
TP_BITE_PS_5V_TS1, TP_BITE_PS_5V_TS2, TP_BITE_PS_12V_TS1, TP_BITE_PS_12V_TS2: RSPRO-1MM-TERMINAL-POST-2622034
TP_BITE_PS_+5V_CURRENT: RSPRO-1MM-TERMINAL-POST-2622034
TP_I2C_NINT, TP_I2C_SCL, TP_I2C_SDA: RSPRO-1MM-TERMINAL-POST-2622034
TP_SPI_CONFIG_CLK: RSPRO-1MM-TERMINAL-POST-2622034
TP_SPI_CONFIG_MISO: RSPRO-1MM-TERMINAL-POST-2622034
TP_SPI_CONFIG_MOSI: RSPRO-1MM-TERMINAL-POST-2622034
TP_SPI_DATA_CLK: RSPRO-1MM-TERMINAL-POST-2622034
TP_SPI_DATA_MOSI: RSPRO-1MM-TERMINAL-POST-2622034
TP_SPI_DATA_NCS: RSPRO-1MM-TERMINAL-POST-2622034
TP_USART_RX: RSPRO-1MM-TERMINAL-POST-2622034
TP_USART_TX: RSPRO-1MM-TERMINAL-POST-2622034
TP_USB_DATA_DM: RSPRO-1MM-TERMINAL-POST-2622034
TP_USB_DATA_DP: RSPRO-1MM-TERMINAL-POST-2622034
TP_VBUS_USB_DATA: RSPRO-1MM-TERMINAL-POST-2622034

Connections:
+3V3_MCU: TP_+3V3_MCU.P$1; also elsewhere on the board
+5V: TP_+5V.P$1; also elsewhere on the board
+12V: TP_+12V.P$1; also elsewhere on the board
-12V: TP_-12V.P$1; also elsewhere on the board
BITE_PS_5V_TS1: TP_BITE_PS_5V_TS1.P$1; also elsewhere on the board
BITE_PS_5V_TS2: TP_BITE_PS_5V_TS2.P$1; also elsewhere on the board
BITE_PS_12V_TS1: TP_BITE_PS_12V_TS1.P$1; also elsewhere on the board
BITE_PS_12V_TS2: TP_BITE_PS_12V_TS2.P$1; also elsewhere on the board
BITE_PS_+5V_CURRENT: TP_BITE_PS_+5V_CURRENT.P$1; also elsewhere on the board
I2C_NINT: TP_I2C_NINT.P$1; also elsewhere on the board
I2C_SCL: TP_I2C_SCL.P$1; also elsewhere on the board
I2C_SDA: TP_I2C_SDA.P$1; also elsewhere on the board
SPI_CONFIG_CLK: TP_SPI_CONFIG_CLK.P$1; also elsewhere on the board
SPI_CONFIG_MISO: TP_SPI_CONFIG_MISO.P$1; also elsewhere on the board
SPI_CONFIG_MOSI: TP_SPI_CONFIG_MOSI.P$1; also elsewhere on the board
SPI_DATA_CLK: TP_SPI_DATA_CLK.P$1; also elsewhere on the board
SPI_DATA_MOSI: TP_SPI_DATA_MOSI.P$1; also elsewhere on the board
SPI_DATA_NCS: TP_SPI_DATA_NCS.P$1; also elsewhere on the board
USART_RX: TP_USART_RX.P$1; also elsewhere on the board
USART_TX: TP_USART_TX.P$1; also elsewhere on the board
USB_DATA_DM: TP_USB_DATA_DM.P$1; also elsewhere on the board
USB_DATA_DP: TP_USB_DATA_DP.P$1; also elsewhere on the board
VBUS_USB_DATA: TP_VBUS_USB_DATA.P$1; also elsewhere on the board

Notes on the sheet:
TESTPINS
pd, 2022
github.com/yildi1337



Board: 2 copper layers, 208.0 x 129.9 mm, 60 parts (54 on the bottom side), 26 nets.

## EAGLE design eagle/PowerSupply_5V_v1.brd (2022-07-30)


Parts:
PCB_BRACKET: 60807-011

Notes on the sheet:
POWER SUPPLY +5 V
pd, 2022
github.com/yildi1337
SHEET ORDER: 02: DIN 41612 CONNECTOR 03: POWER SUPPLY +5 V


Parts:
CON_BACKPLANE: 09031326921
TP_GND1, TP_GND2, TP_GND3, TP_GND4: RSPRO-1MM-TERMINAL-POST-2622034
TS1, TS2: NB-PTCO-160

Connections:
+5V: CON_BACKPLANE.1, CON_BACKPLANE.2; also elsewhere on the board
+12V: CON_BACKPLANE.5
-12V: CON_BACKPLANE.6
BITE_PS_5V_TS1: CON_BACKPLANE.11, TS1.1
BITE_PS_5V_TS2: CON_BACKPLANE.12, TS2.1
BITE_PS_12V_TS1: CON_BACKPLANE.13
BITE_PS_12V_TS2: CON_BACKPLANE.14
BITE_PS_+5V_CURRENT: CON_BACKPLANE.9; also elsewhere on the board
GND: CON_BACKPLANE.3, CON_BACKPLANE.4, CON_BACKPLANE.7, CON_BACKPLANE.8, CON_BACKPLANE.10, CON_BACKPLANE.15, CON_BACKPLANE.16, CON_BACKPLANE.17, CON_BACKPLANE.18, CON_BACKPLANE.19, CON_BACKPLANE.20, CON_BACKPLANE.21, CON_BACKPLANE.22, CON_BACKPLANE.23, CON_BACKPLANE.24, CON_BACKPLANE.29, CON_BACKPLANE.30, CON_BACKPLANE.31, CON_BACKPLANE.32, TP_GND1.P$1, TP_GND2.P$1, TP_GND3.P$1, TP_GND4.P$1, TS1.2, TS2.2; also elsewhere on the board
L: CON_BACKPLANE.27, CON_BACKPLANE.28; also elsewhere on the board
N: CON_BACKPLANE.25, CON_BACKPLANE.26; also elsewhere on the board

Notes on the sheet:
DIN 41612 CONNECTOR
pd, 2022
github.com/yildi1337


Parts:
BR1: GBJ610
C1, C2, C3, C4: 10n/1kV; C1808
C5, C6, C7, C8, C9, C10, C11, C12, C13: 15000u/16V; EEUHD1C153
C14: 10u/16V; 153CLV-0405
C15, C17, C18, C20, C21, C22: 100n; C0603
C16: 1000u/16V; 153CLV-1010
C19: 470n; C0603
FUSE_+5V: 0031.8201
HS1: FK 237 SA 220 O; FK_237_SA_220_O
IC1: MIC29300-5.0WT
IC2: ACS712ELCTR-05B-T
LED_+5V_OK: 113-314-04
OP1: MCP6L1T-E/OT
R1: 82/2W; R2010
R2: 150; R0603
R3: 0; R0603
R4: 3k; R0603
R5: 2k; R0603
R6, R7: 100k; R0603
R8: 27k; R0603
SWITCH_+5V: RSPRO-SPDT-SLIDE-SWITCH-7347334
TF1: FL 24/6; FL_24-6
TP_+5V: RSPRO-1MM-TERMINAL-POST-2622034
TP_BITE_PS_+5V_CURRENT: RSPRO-1MM-TERMINAL-POST-2622034
TP_HALL_SENSOR_VIOUT: RSPRO-1MM-TERMINAL-POST-2622034
TP_RECT_OUT: RSPRO-1MM-TERMINAL-POST-2622034
TP_TF_SEC_A: RSPRO-1MM-TERMINAL-POST-2622034
TP_TF_SEC_B: RSPRO-1MM-TERMINAL-POST-2622034

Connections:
+5V: C18.1, C22.1, FUSE_+5V.2, IC2.8 (VCC), OP1.2 (VDD), R2.2, R7.2; also elsewhere on the board
BITE_PS_+5V_CURRENT: C21.1, OP1.1 (VOUT), R8.2, TP_BITE_PS_+5V_CURRENT.P$1; also elsewhere on the board
GND: BR1.-, C1.2, C3.1, C5.-, C6.-, C7.-, C8.-, C9.-, C10.-, C11.-, C12.-, C13.-, C14.-, C15.2, C16.-, C17.2, C18.2, C19.2, C20.2, C21.2, C22.2, IC1.2 (GND), IC2.5 (GND), LED_+5V_OK.- (C), OP1.5 (VSS), R1.1, R6.1; also elsewhere on the board
L: TF1.P1A; also elsewhere on the board
N: TF1.P2B; also elsewhere on the board
unnamed: C19.1, IC2.6 (FILTER)
unnamed: FUSE_+5V.1, IC2.3 (IP-), IC2.4 (IP-), R3.2
unnamed: BR1.+, C2.2, C4.1, C5.+, C6.+, C7.+, C8.+, C9.+, C10.+, C11.+, C12.+, C13.+, R1.2, SWITCH_+5V.3 (NO), TP_RECT_OUT.P$1
unnamed: IC2.7 (VIOUT), R4.1, TP_HALL_SENSOR_VIOUT.P$1
unnamed: TF1.P1B, TF1.P2A
unnamed: BR1.L, C1.1, C2.1, TF1.S1A, TF1.S2A, TP_TF_SEC_A.P$1
unnamed: LED_+5V_OK.+ (A), R2.1
unnamed: C16.+, C17.1, IC1.3 (OUT), IC2.1 (IP+), IC2.2 (IP+), R3.1, TP_+5V.P$1
unnamed: R4.2, R5.1
unnamed: BR1.N, C3.2, C4.2, TF1.S1B, TF1.S2B, TP_TF_SEC_B.P$1
unnamed: C20.1, OP1.3 (VIN+), R6.2, R7.1
unnamed: C14.+, C15.1, IC1.1 (IN), SWITCH_+5V.2 (COM)
unnamed: OP1.4 (VIN-), R5.2, R8.1

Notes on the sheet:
POWER SUPPLY +5 V
pd, 2022
github.com/yildi1337
9 x EEUHD1C153
4 x 1808AC103KAT2A
n.c.
2.5 V +/- 185 mV/A
2.5 V -/+ 1000 mV/A
Gain: 5.4


Board: 2 copper layers, 160.0 x 100.0 mm, 53 parts (0 on the bottom side), 20 nets.

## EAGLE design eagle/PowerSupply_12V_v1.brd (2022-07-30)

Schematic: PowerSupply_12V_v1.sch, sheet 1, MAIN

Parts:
PCB_BRACKET: 60807-011

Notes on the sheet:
POWER SUPPLY +/-12 V
pd, 2022
github.com/yildi1337
SHEET ORDER: 02: DIN 41612 CONNECTOR 03: POWER SUPPLY +/-12 V

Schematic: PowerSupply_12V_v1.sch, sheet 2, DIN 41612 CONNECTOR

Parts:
CON_BACKPLANE: 09031326921
TP_GND1, TP_GND2, TP_GND3, TP_GND4: RSPRO-1MM-TERMINAL-POST-2622034
TS1, TS2: NB-PTCO-160

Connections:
+5V: CON_BACKPLANE.1, CON_BACKPLANE.2
+12V: CON_BACKPLANE.5; also elsewhere on the board
-12V: CON_BACKPLANE.6; also elsewhere on the board
BITE_PS_5V_TS1: CON_BACKPLANE.11
BITE_PS_5V_TS2: CON_BACKPLANE.12
BITE_PS_12V_TS1: CON_BACKPLANE.13, TS1.1
BITE_PS_12V_TS2: CON_BACKPLANE.14, TS2.1
BITE_PS_+5V_CURRENT: CON_BACKPLANE.9
GND: CON_BACKPLANE.3, CON_BACKPLANE.4, CON_BACKPLANE.7, CON_BACKPLANE.8, CON_BACKPLANE.10, CON_BACKPLANE.15, CON_BACKPLANE.16, CON_BACKPLANE.17, CON_BACKPLANE.18, CON_BACKPLANE.19, CON_BACKPLANE.20, CON_BACKPLANE.21, CON_BACKPLANE.22, CON_BACKPLANE.23, CON_BACKPLANE.24, CON_BACKPLANE.29, CON_BACKPLANE.30, CON_BACKPLANE.31, CON_BACKPLANE.32, TP_GND1.P$1, TP_GND2.P$1, TP_GND3.P$1, TP_GND4.P$1, TS1.2, TS2.2; also elsewhere on the board
L: CON_BACKPLANE.27, CON_BACKPLANE.28; also elsewhere on the board
N: CON_BACKPLANE.25, CON_BACKPLANE.26; also elsewhere on the board

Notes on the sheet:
DIN 41612 CONNECTOR
pd, 2022
github.com/yildi1337

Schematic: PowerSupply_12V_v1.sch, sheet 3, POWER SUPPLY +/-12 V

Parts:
BR1: GBJ610
C1, C2, C3, C4: 10n/1kV; C1808
C5, C6, C7, C8, C9, C10: 10000u/25V; EEUHD1E103
C11, C15: 22u/25V; 153CLV-0505
C12, C14, C16, C18: 100n; C0603
C13, C17: 100u/25V; 153CLV-0810
FUSE_+12V: 0031.8201
FUSE_-12V: 0031.8201
HS1, HS2: FK 237 SA 220 O; FK_237_SA_220_O
IC1: LM1085IT-12
IC2: LM2990T-12
LED_+12V_OK: 113-314-04
LED_-12V_OK: 113-314-04
R1, R3: 360/2W; R2010
R2, R4: 680; R0603
SWITCH_+12V: RSPRO-SPDT-SLIDE-SWITCH-7347334
SWITCH_-12V: RSPRO-SPDT-SLIDE-SWITCH-7347334
TF1: FL 24/12; FL_24-12
TP_+12V: RSPRO-1MM-TERMINAL-POST-2622034
TP_-12V: RSPRO-1MM-TERMINAL-POST-2622034
TP_RECT_OUT+: RSPRO-1MM-TERMINAL-POST-2622034
TP_RECT_OUT-: RSPRO-1MM-TERMINAL-POST-2622034
TP_TF_SEC_A: RSPRO-1MM-TERMINAL-POST-2622034
TP_TF_SEC_B: RSPRO-1MM-TERMINAL-POST-2622034

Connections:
+12V: FUSE_+12V.2, R2.2; also elsewhere on the board
-12V: FUSE_-12V.2, R4.1; also elsewhere on the board
GND: C5.-, C6.-, C7.-, C8.+, C9.+, C10.+, C11.-, C12.2, C13.-, C14.2, C15.+, C16.1, C17.+, C18.1, IC1.1 (GND), IC2.1 (GND), LED_+12V_OK.- (C), LED_-12V_OK.+ (A), R1.1, R3.2, TF1.S1B, TF1.S2A; also elsewhere on the board
L: TF1.P1A; also elsewhere on the board
N: TF1.P2B; also elsewhere on the board
unnamed: C15.-, C16.2, IC2.2 (IN), SWITCH_-12V.1 (NC), SWITCH_-12V.2 (COM)
unnamed: LED_-12V_OK.- (C), R4.2
unnamed: C17.-, C18.2, FUSE_-12V.1, IC2.3 (OUT), TP_-12V.P$1
unnamed: TF1.P1B, TF1.P2A
unnamed: BR1.L, C1.1, C2.1, TF1.S1A, TP_TF_SEC_A.P$1
unnamed: LED_+12V_OK.+ (A), R2.1
unnamed: C13.+, C14.1, FUSE_+12V.1, IC1.2 (OUT), TP_+12V.P$1
unnamed: BR1.N, C3.2, C4.2, TF1.S2B, TP_TF_SEC_B.P$1
unnamed: C11.+, C12.1, IC1.3 (IN), SWITCH_+12V.1 (NC), SWITCH_+12V.2 (COM)
RECT_OUT+: BR1.+, C2.2, C4.1, C5.+, C6.+, C7.+, R1.2, SWITCH_+12V.3 (NO), TP_RECT_OUT+.P$1
RECT_OUT-: BR1.-, C1.2, C3.1, C8.-, C9.-, C10.-, R3.1, SWITCH_-12V.3 (NO), TP_RECT_OUT-.P$1

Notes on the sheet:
POWER SUPPLY +/-12 V
pd, 2022
github.com/yildi1337
4 x 1808AC103KAT2A
6 x EEUHD1E103
500mA


Board: 2 copper layers, 160.0 x 100.0 mm, 48 parts (0 on the bottom side), 19 nets.

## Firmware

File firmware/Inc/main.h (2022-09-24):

/*
 *******************************************************************************
 * File:			main.h
 * Date:			2022-04-10
 * Author:			Phillip Durdaut
 * Summary:			Main include file with main program definitions
 * Notes:			-
 *******************************************************************************
 */

/* Define to prevent recursive inclusion -------------------------------------*/
#ifndef __MAIN_H
#define __MAIN_H

/* Includes ------------------------------------------------------------------*/
#include <stdio.h>
#include <stdlib.h>
#include <string.h>
#include <stdbool.h>
#include <stdint.h>
#include <float.h>
#include <ctype.h>

#include "stm32h7xx.h"
#include "stm32h7xx_hal.h"
#include "stm32h7xx_it.h"

#include "tca9534a.h"

/* Public defines ------------------------------------------------------------*/

/* ADC */
#define MAIN_ADC_SAMPLES_PER_SECOND						256e3
#define MAIN_ADC_SAMPLES_PER_MILLI_SECOND				256
#define MAIN_ADC_NUM_CHANNELS							4
#define MAIN_ADC_BYTES_PER_SAMPLE_PER_CHANNEL			4
#define MAIN_ADC_BYTES_PER_SAMPLE						(MAIN_ADC_NUM_CHANNELS * MAIN_ADC_BYTES_PER_SAMPLE_PER_CHANNEL)
#define MAIN_ADC_BYTES_PER_SECOND_PER_CHANNEL			(MAIN_ADC_BYTES_PER_SAMPLE_PER_CHANNEL * MAIN_ADC_SAMPLES_PER_SECOND)
#define MAIN_ADC_BYTES_PER_SECOND						(MAIN_ADC_NUM_CHANNELS * MAIN_ADC_BYTES_PER_SAMPLE_PER_CHANNEL * MAIN_ADC_SAMPLES_PER_SECOND)
#define MAIN_ADC_BYTES_PER_MILLI_SECOND_PER_CHANNEL		(MAIN_ADC_BYTES_PER_SAMPLE_PER_CHANNEL * MAIN_ADC_SAMPLES_PER_MILLI_SECOND)
#define MAIN_ADC_BYTES_PER_MILLI_SECOND					(MAIN_ADC_NUM_CHANNELS * MAIN_ADC_BYTES_PER_SAMPLE_PER_CHANNEL * MAIN_ADC_SAMPLES_PER_MILLI_SECOND)
#define MAIN_ADC_CLIPPING_VALUE							(4194304+100000)	/* slightly above 2.5 V */

/* USB */
#define MAIN_USB_VENDOR_ID								0x1337
#define MAIN_USB_PRODUCT_ID								0x0011
#define MAIN_USB_LANG_ID_STRING_US		 				0x0409
#define MAIN_USB_LANG_ID_STRING_DE		 				0x0407
#define MAIN_USB_LANG_ID_STRING							MAIN_USB_LANG_ID_STRING_US
#define MAIN_USB_MANUFACTURER_STRING	  				"pd"
#define MAIN_USB_PRODUCT_STRING							"DAQ v3"
#define MAIN_USB_SERIAL_STRING	 						"0000"
#define MAIN_USB_CONFIGURATION_STRING  					"DAQ v3 Config"
#define MAIN_USB_INTERFACE_STRING	  					"DAQ v3 Interface"
#define MAIN_USB_DEVICE_VERSION							0x0100

/* Interrupt priorities */
#define IRQ_UART1_PREEMPT_PRIORITY				2
#define IRQ_UART1_SUB_PRIORITY					2
#define IRQ_DMA1_STREAM0_PREEMPT_PRIORITY		10
#define IRQ_DMA1_STREAM0_SUB_PRIORITY			10
#define IRQ_OTG_HS_EP1_OUT_PREEMPT_PRIORITY		5
#define IRQ_OTG_HS_EP1_OUT_SUB_PRIORITY			5
#define IRQ_OTG_HS_EP1_IN_PREEMPT_PRIORITY		5
#define IRQ_OTG_HS_EP1_IN_SUB_PRIORITY			5
#define IRQ_OTG_HS_PREEMPT_PRIORITY				5
#define IRQ_OTG_HS_SUB_PRIORITY					5

/* Pins and ports */
#define LED_1_Pin 											GPIO_PIN_2
#define LED_1_Port 											GPIOE
#define LED_2_Pin 											GPIO_PIN_3
#define LED_2_Port 											GPIOE
#define LED_3_Pin 											GPIO_PIN_4
#define LED_3_Port 											GPIOE
#define LED_4_Pin 											GPIO_PIN_5
#define LED_4_Port 											GPIOE

#define DEBUG_1_Pin 										GPIO_PIN_10
#define DEBUG_1_Port 										GPIOE
#define DEBUG_2_Pin 										GPIO_PIN_11
#define DEBUG_2_Port 										GPIOE
#define DEBUG_3_Pin 										GPIO_PIN_12
#define DEBUG_3_Port 										GPIOE
#define DEBUG_4_Pin 										GPIO_PIN_13
#define DEBUG_4_Port 										GPIOE

#define UART1_TX_Pin										GPIO_PIN_6
#define UART1_TX_Port 										GPIOB
#define UART1_TX_AF 										GPIO_AF7_USART1
#define UART1_RX_Pin										GPIO_PIN_7
#define UART1_RX_Port 										GPIOB
#define UART1_RX_AF 										GPIO_AF7_USART1

#define SPI2_NSS_Pin 										GPIO_PIN_9
#define SPI2_NSS_Port 										GPIOB
#define SPI2_NSS_AF											GPIO_AF5_SPI2
#define SPI2_SCK_Pin 										GPIO_PIN_3
#define SPI2_SCK_Port 										GPIOD
#define SPI2_SCK_AF											GPIO_AF5_SPI2
#define SPI2_MOSI_Pin 										GPIO_PIN_15
#define SPI2_MOSI_Port 										GPIOB
#define SPI2_MOSI_AF										GPIO_AF5_SPI2

#define SPI3_SCK_Pin 										GPIO_PIN_10
#define SPI3_SCK_Port 										GPIOC
#define SPI3_SCK_AF											GPIO_AF6_SPI3
#define SPI3_MISO_Pin 										GPIO_PIN_11
#define SPI3_MISO_Port 										GPIOC
#define SPI3_MISO_AF										GPIO_AF6_SPI3
#define SPI3_MOSI_Pin 										GPIO_PIN_6
#define SPI3_MOSI_Port 										GPIOD
#define SPI3_MOSI_AF										GPIO_AF5_SPI3

#define USB_OTG_HS_ULPI_STP_Pin 							GPIO_PIN_0
#define USB_OTG_HS_ULPI_STP_Port 							GPIOC
#define USB_OTG_HS_ULPI_STP_AF								GPIO_AF10_OTG2_HS
#define USB_OTG_HS_ULPI_DIR_Pin 							GPIO_PIN_2
#define USB_OTG_HS_ULPI_DIR_Port 							GPIOC
#define USB_OTG_HS_ULPI_DIR_AF								GPIO_AF10_OTG2_HS
#define USB_OTG_HS_ULPI_NXT_Pin 							GPIO_PIN_3
#define USB_OTG_HS_ULPI_NXT_Port 							GPIOC
#define USB_OTG_HS_ULPI_NXT_AF								GPIO_AF10_OTG2_HS
#define USB_OTG_HS_ULPI_CK_Pin 								GPIO_PIN_5
#define USB_OTG_HS_ULPI_CK_Port 							GPIOA
#define USB_OTG_HS_ULPI_CK_AF								GPIO_AF10_OTG2_HS
#define USB_OTG_HS_ULPI_D0_Pin 								GPIO_PIN_3
#define USB_OTG_HS_ULPI_D0_Port 							GPIOA
#define USB_OTG_HS_ULPI_D0_AF								GPIO_AF10_OTG2_HS
#define USB_OTG_HS_ULPI_D1_Pin 								GPIO_PIN_0
#define USB_OTG_HS_ULPI_D1_Port 							GPIOB
#define USB_OTG_HS_ULPI_D1_AF								GPIO_AF10_OTG2_HS
#define USB_OTG_HS_ULPI_D2_Pin 								GPIO_PIN_1
#define USB_OTG_HS_ULPI_D2_Port 							GPIOB
#define USB_OTG_HS_ULPI_D2_AF								GPIO_AF10_OTG2_HS
#define USB_OTG_HS_ULPI_D3_Pin 								GPIO_PIN_10
#define USB_OTG_HS_ULPI_D3_Port 							GPIOB
#define USB_OTG_HS_ULPI_D3_AF								GPIO_AF10_OTG2_HS
#define USB_OTG_HS_ULPI_D4_Pin 								GPIO_PIN_11
#define USB_OTG_HS_ULPI_D4_Port 							GPIOB
#define USB_OTG_HS_ULPI_D4_AF								GPIO_AF10_OTG2_HS
#define USB_OTG_HS_ULPI_D5_Pin 								GPIO_PIN_12
#define USB_OTG_HS_ULPI_D5_Port 							GPIOB
#define USB_OTG_HS_ULPI_D5_AF								GPIO_AF10_OTG2_HS
#define USB_OTG_HS_ULPI_D6_Pin 								GPIO_PIN_13
#define USB_OTG_HS_ULPI_D6_Port 							GPIOB
#define USB_OTG_HS_ULPI_D6_AF								GPIO_AF10_OTG2_HS
#define USB_OTG_HS_ULPI_D7_Pin 								GPIO_PIN_5
#define USB_OTG_HS_ULPI_D7_Port 							GPIOB
#define USB_OTG_HS_ULPI_D7_AF								GPIO_AF10_OTG2_HS

#define I2C4_SCL_Port										GPIOD
#define I2C4_SCL_Pin										GPIO_PIN_12
#define I2C4_SCL_AF											GPIO_AF4_I2C4
#define I2C4_SDA_Port										GPIOD
#define I2C4_SDA_Pin										GPIO_PIN_13
#define I2C4_SDA_AF											GPIO_AF4_I2C4

/* I/O expander */
#define ADC_NRESET_DEVICE									TCA9534A_DEVICE_ACNV
#define ADC_NRESET_PIN										TCA9534A_PIN_0
#define ADC_SPI_NCS_DEVICE									TCA9534A_DEVICE_ACNV
#define ADC_SPI_NCS_PIN										TCA9534A_PIN_1
#define RD_NCS_DEVICE										TCA9534A_DEVICE_ACNV
#define RD_NCS_PIN											TCA9534A_PIN_2
#define RD_NRESET_DEVICE									TCA9534A_DEVICE_ACNV
#define RD_NRESET_PIN										TCA9534A_PIN_3

/* Public macros -------------------------------------------------------------*/
/* Public typedefs -----------------------------------------------------------*/
typedef uint8_t flag_t;
typedef enum
{
	CHANNEL_1 = 0,
	CHANNEL_2 = 1,
	CHANNEL_NONE
} channel_t;

/* Public variables ----------------------------------------------------------*/
extern flag_t MAIN_MeasurementRunning;
extern flag_t MAIN_SamplesRequested;

/* Public function prototypes ------------------------------------------------*/
extern void Error_Handler(void);

#endif /* __MAIN_H */

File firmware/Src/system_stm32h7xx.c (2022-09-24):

/**
  ******************************************************************************
  * @file	system_stm32h7xx.c
  * @author  MCD Application Team
  * @brief   CMSIS Cortex-Mx Device Peripheral Access Layer System Source File.
  *
  *   This file provides two functions and one global variable to be called from
  *   user application:
  *	  - SystemInit(): This function is called at startup just after reset and
  *					  before branch to main program. This call is made inside
  *					  the "startup_stm32h7xx.s" file.
  *
  *	  - SystemCoreClock variable: Contains the core clock, it can be used
  *								  by the user application to setup the SysTick
  *								  timer or configure other parameters.
  *
  *	  - SystemCoreClockUpdate(): Updates the variable SystemCoreClock and must
  *								 be called whenever the core clock is changed
  *								 during program execution.
  *
  *
  ******************************************************************************
  * @attention
  *
  * <h2><center>&copy; Copyright (c) 2017 STMicroelectronics.
  * All rights reserved.</center></h2>
  *
  * This software component is licensed by ST under BSD 3-Clause license,
  * the "License"; You may not use this file except in compliance with the
  * License. You may obtain a copy of the License at:
  *						opensource.org/licenses/BSD-3-Clause
  *
  ******************************************************************************
  */

/** @addtogroup CMSIS
  * @{
  */

/** @addtogroup stm32h7xx_system
  * @{
  */

/** @addtogroup STM32H7xx_System_Private_Includes
  * @{
  */

#include "stm32h7xx.h"
#include <math.h>
#if !defined  (HSE_VALUE)
#define HSE_VALUE	((uint32_t)25000000) /*!< Value of the External oscillator in Hz */
#endif /* HSE_VALUE */

#if !defined  (CSI_VALUE)
  #define CSI_VALUE	((uint32_t)4000000) /*!< Value of the Internal oscillator in Hz*/
#endif /* CSI_VALUE */

#if !defined  (HSI_VALUE)
  #define HSI_VALUE	((uint32_t)64000000) /*!< Value of the Internal oscillator in Hz*/
#endif /* HSI_VALUE */


/**
  * @}
  */

/** @addtogroup STM32H7xx_System_Private_TypesDefinitions
  * @{
  */

/**
  * @}
  */

/** @addtogroup STM32H7xx_System_Private_Defines
  * @{
  */

/************************* Miscellaneous Configuration ************************/
/*!< Uncomment the following line if you need to use initialized data in D2 domain SRAM (AHB SRAM) */
/* #define DATA_IN_D2_SRAM */

/*!< Uncomment the following line if you need to relocate your vector Table in
	 Internal SRAM. */
/* #define VECT_TAB_SRAM */
#define VECT_TAB_OFFSET  0x00000000UL /*!< Vector Table base offset field.
									  This value must be a multiple of 0x200. */
/******************************************************************************/

/**
  * @}
  */

/** @addtogroup STM32H7xx_System_Private_Macros
  * @{
  */

/**
  * @}
  */

/** @addtogroup STM32H7xx_System_Private_Variables
  * @{
  */
  /* This variable is updated in three ways:
	  1) by calling CMSIS function SystemCoreClockUpdate()
	  2) by calling HAL API function HAL_RCC_GetHCLKFreq()
	  3) each time HAL_RCC_ClockConfig() is called to configure the system clock frequency
		 Note: If you use this function to configure the system clock; then there
			   is no need to call the 2 first functions listed above, since SystemCoreClock
			   variable is updated automatically.
  */
  uint32_t SystemCoreClock = 64000000;
  uint32_t SystemD2Clock = 64000000;
  const  uint8_t D1CorePrescTable[16] = {0, 0, 0, 0, 1, 2, 3, 4, 1, 2, 3, 4, 6, 7, 8, 9};

/**
  * @}
  */

/** @addtogroup STM32H7xx_System_Private_FunctionPrototypes
  * @{
  */

/**
  * @}
  */

/** @addtogroup STM32H7xx_System_Private_Functions
  * @{
  */

/**
  * @brief  Setup the microcontroller system
  *		 Initialize the FPU setting and  vector table location
  *		 configuration.
  * @param  None
  * @retval None
  */
void SystemInit (void)
{
#if defined (DATA_IN_D2_SRAM)
 __IO uint32_t tmpreg;
#endif /* DATA_IN_D2_SRAM */

  /* FPU settings ------------------------------------------------------------*/
  #if (__FPU_PRESENT == 1) && (__FPU_USED == 1)
	SCB->CPACR |= ((3UL << (10*2))|(3UL << (11*2)));  /* set CP10 and CP11 Full Access */
  #endif
  /* Reset the RCC clock configuration to the default reset state ------------*/

   /* Increasing the CPU frequency */
  if(FLASH_LATENCY_DEFAULT  > (READ_BIT((FLASH->ACR), FLASH_ACR_LATENCY)))
  {
	/* Program the new number of wait states to the LATENCY bits in the FLASH_ACR register */
	MODIFY_REG(FLASH->ACR, FLASH_ACR_LATENCY, (uint32_t)(FLASH_LATENCY_DEFAULT));
  }

  /* Set HSION bit */
  RCC->CR |= RCC_CR_HSION;

  /* Reset CFGR register */
  RCC->CFGR = 0x00000000;

  /* Reset HSEON, HSECSSON, CSION, HSI48ON, CSIKERON, PLL1ON, PLL2ON and PLL3ON bits */
  RCC->CR &= 0xEAF6ED7FU;
  
   /* Decreasing the number of wait states because of lower CPU frequency */
  if(FLASH_LATENCY_DEFAULT  < (READ_BIT((FLASH->ACR), FLASH_ACR_LATENCY)))
  {
	/* Program the new number of wait states to the LATENCY bits in the FLASH_ACR register */
	MODIFY_REG(FLASH->ACR, FLASH_ACR_LATENCY, (uint32_t)(FLASH_LATENCY_DEFAULT));
  }

#if defined(D3_SRAM_BASE)
  /* Reset D1CFGR register */
  RCC->D1CFGR = 0x00000000;

  /* Reset D2CFGR register */
  RCC->D2CFGR = 0x00000000;

  /* Reset D3CFGR register */
  RCC->D3CFGR = 0x00000000;
#else
  /* Reset CDCFGR1 register */
  RCC->CDCFGR1 = 0x00000000;

  /* Reset CDCFGR2 register */
  RCC->CDCFGR2 = 0x00000000;

  /* Reset SRDCFGR register */
  RCC->SRDCFGR = 0x00000000;
#endif
  /* Reset PLLCKSELR register */
  RCC->PLLCKSELR = 0x02020200;

  /* Reset PLLCFGR register */
  RCC->PLLCFGR = 0x01FF0000;
  /* Reset PLL1DIVR register */
  RCC->PLL1DIVR = 0x01010280;
  /* Reset PLL1FRACR register */
  RCC->PLL1FRACR = 0x00000000;

  /* Reset PLL2DIVR register */
  RCC->PLL2DIVR = 0x01010280;

  /* Reset PLL2FRACR register */

  RCC->PLL2FRACR = 0x00000000;
  /* Reset PLL3DIVR register */
  RCC->PLL3DIVR = 0x01010280;

  /* Reset PLL3FRACR register */
  RCC->PLL3FRACR = 0x00000000;

  /* Reset HSEBYP bit */
  RCC->CR &= 0xFFFBFFFFU;

  /* Disable all interrupts */
  RCC->CIER = 0x00000000;

#if (STM32H7_DEV_ID == 0x450UL)
  /* dual core CM7 or single core line */
  if((DBGMCU->IDCODE & 0xFFFF0000U) < 0x20000000U)
  {
	/* if stm32h7 revY*/
	/* Change  the switch matrix read issuing capability to 1 for the AXI SRAM target (Target 7) */
	*((__IO uint32_t*)0x51008108) = 0x000000001U;
  }
#endif

#if defined (DATA_IN_D2_SRAM)
  /* in case of initialized data in D2 SRAM (AHB SRAM) , enable the D2 SRAM clock (AHB SRAM clock) */
#if defined(RCC_AHB2ENR_D2SRAM3EN)
  RCC->AHB2ENR |= (RCC_AHB2ENR_D2SRAM1EN | RCC_AHB2ENR_D2SRAM2EN | RCC_AHB2ENR_D2SRAM3EN);
#elif defined(RCC_AHB2ENR_D2SRAM2EN)
  RCC->AHB2ENR |= (RCC_AHB2ENR_D2SRAM1EN | RCC_AHB2ENR_D2SRAM2EN);
#else
  RCC->AHB2ENR |= (RCC_AHB2ENR_AHBSRAM1EN | RCC_AHB2ENR_AHBSRAM2EN);
#endif /* RCC_AHB2ENR_D2SRAM3EN */

  tmpreg = RCC->AHB2ENR;
  (void) tmpreg;
#endif /* DATA_IN_D2_SRAM */

#if defined(DUAL_CORE) && defined(CORE_CM4)
  /* Configure the Vector Table location add offset address for cortex-M4 ------------------*/
#ifdef VECT_TAB_SRAM
  SCB->VTOR = D2_AXISRAM_BASE | VECT_TAB_OFFSET; /* Vector Table Relocation in Internal SRAM */
#else
  SCB->VTOR = FLASH_BANK2_BASE | VECT_TAB_OFFSET; /* Vector Table Relocation in Internal FLASH */
#endif /* VECT_TAB_SRAM */
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

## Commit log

2022-07-30 Added pictures of the bare boards
2022-07-30 Added EAGLE project files
    [AnalogConversion_v1.brd, AnalogConversion_v1.sch, AnalogConversion_v2.brd, AnalogConversion_v2.sch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]
2022-07-30 Added complete CAD model
    [0031.8201.ipt, 09031326921.ipt, 09032326825.ipt, 1-copper.ipt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]
2022-08-11 Minor changes to 3D model
    [KMF1.1211.11.ipt, Packages.iam, RibbonCableConnector_2x5.iam, RibbonCableConnector_2x5.ipt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]

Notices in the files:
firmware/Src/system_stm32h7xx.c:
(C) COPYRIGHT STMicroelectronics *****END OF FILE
